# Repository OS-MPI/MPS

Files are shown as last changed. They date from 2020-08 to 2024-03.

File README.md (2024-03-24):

# The Magnetic Particle Spectroscopy (MPS) device
# [Link to the wiki](https://github.com/OS-MPI/MPS/wiki)
# [Link to the Main OS-MPI Page](https://os-mpi.github.io/)

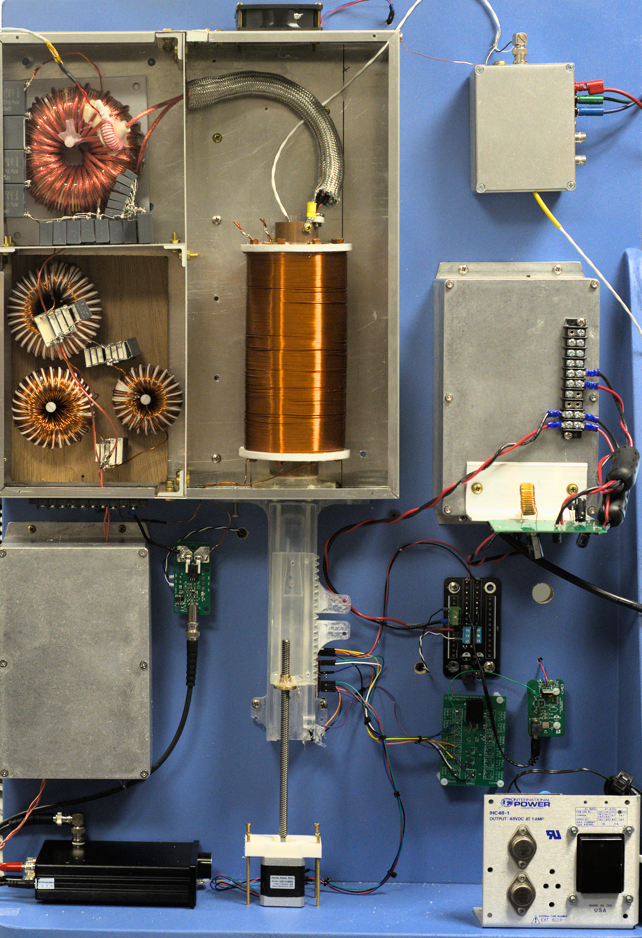
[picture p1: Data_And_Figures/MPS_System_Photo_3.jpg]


## Motivation and Introduction

The system we are calling the MPS device is a low cost, and fairly simple to manufacture project which more generally speaking is a platform designed around understanding magnetic characteristics of superparamagentic iron oxide nanoparticles (SPIONs). The motivation was to condense the numerous existing systems into a singlular platform capable of providing insights into the nanoparticles irrespective of the specific goal of the lab. With that in mind, calling our platform an "MPS" system is rather imprecise; while one mode is traditional "spectroscopy" the device is designed to be flexible and able to perform relaxometry measurements as well as magnetometry, yet in order to give the project an easy-to-find, descriptive name, we settled on the "magnetic particle spectroscopy" system. 

## State of the project

In the current state (of March 2024) we have the system working in all [primary operational modes](https://github.com/OS-MPI/MPS/wiki/Modes-of-operation). It is capable of sensitively detecting SPIONs to the ng Fe level, quantifying the magnetization spectra, tracing the hysteresis loops, etc. 

The primary focus now is improving the documentation.

## System overview

Broadly speaking, there are four principle hardware components, the three coils (drive, receive, and bias) and the sample positioner. The drive coils produce magnetic fields (typ. 10 mT) which cause the SPIONs within the bore to go into and out of saturation at 23.8 kHz. This changing magnetism induces a voltage in the receive coils. The bias coils allow for the quasistatic operating point of the SPIONs to be modulated by generating low frequency (~10 Hz) fields up to about 50 mT.

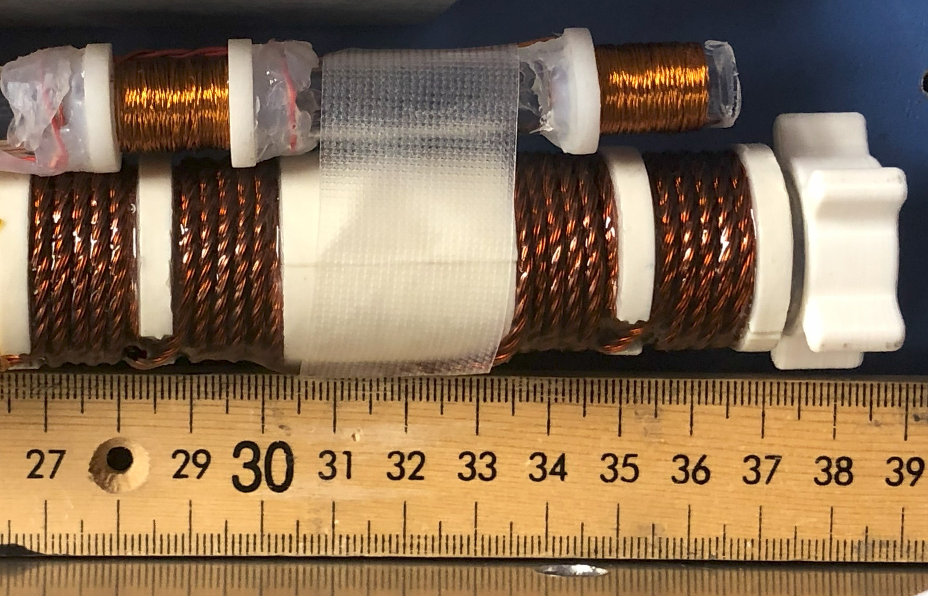
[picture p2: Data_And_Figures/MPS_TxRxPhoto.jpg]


### Drive/Transmit system
The drive system consists of the drive coils as well as the amplifier and filter. 

The drive coil is seen in the photograph above (the larger coil with four sub-sections). All of the four winding sections are in the same handedness. See the Wiki for further details. 

In this photograph, we utilize an in-house made Litz wire (18 strands of 28 AWG magnet wire), although other Litz wires may work similarly well. Previously a commercial Litz wire with 115 strands of 36AWG was used, but because of the plastic sleeve over the wires, they could not be easily stabilized with epoxy. 

The drive filter serves to purify and the waveform produced by the amplifier. Most amplifiers produce about 0.1% (or worse) total harmonic distortion, so without this filter those amplifier-generated distortions will dominate the noise floor. That being said, its among the most challenging components to manufacture, so its worth discussing which components are essential, and which are more or less optional. Refering to the schematic below, the two most important sections are the tuning/matching capacitors (C1 and C2), and the transformer (LPri and LSec). The tuning capacitors form a resonant circuit with Ldrive (the drive coil's equivalent load). This can be seen if you notice the loop formed by C1 C2 and LDrive is resonant. The choice of values for C1 and C2 is to make the equivalent impedance 8 ohms or so. The transformer should be a ferrite such as N87 and be designed such that the core flux is well below saturation (~20x lower, so 20ish mT). The purpose is to mitigate common-mode noise and provide isolation/break any ground loops. The other filter components can be "dropped in" later without disturbing the overall circuit. But these additional filtering components are both the most challenging to build, and less necessary. 
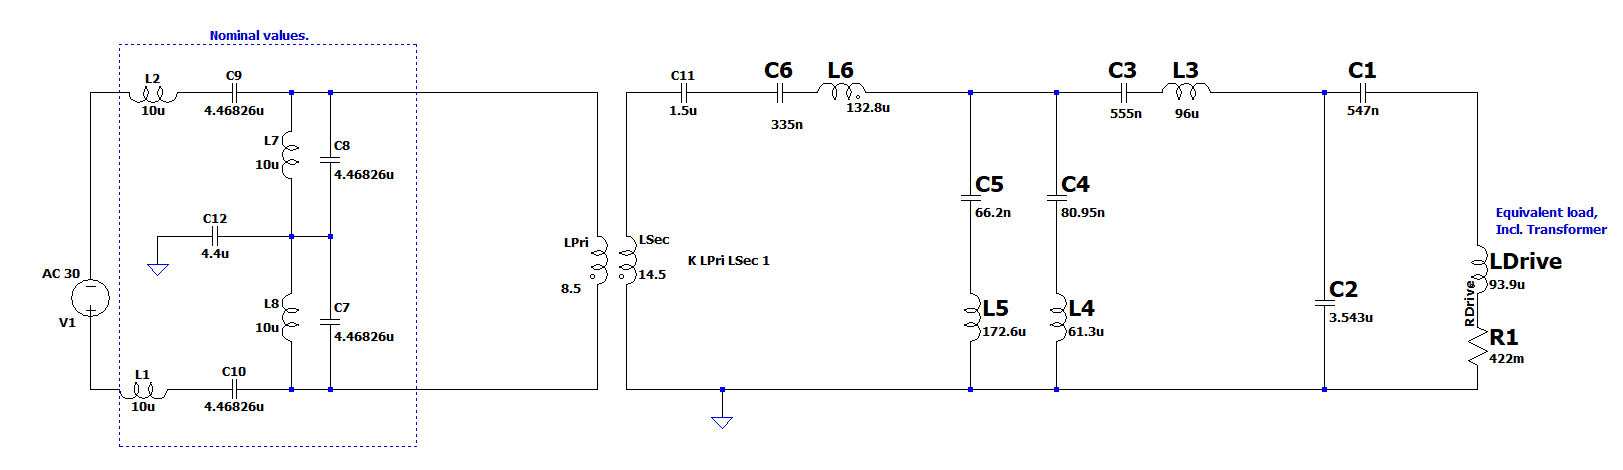
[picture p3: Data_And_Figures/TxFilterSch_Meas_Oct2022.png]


Many different drive amplifiers can be used. We have used both linear and switch-mode amplifiers with success. For a basic system, the AIYIMA A07 can be used, or other amplifiers based on the TPA3255 will likely be good choices. For example Nobsound G2 pro is also likely good and is pre-configured to be in PBTL mode. That IC from Texas Instruments has excellent performance given the cost and high switching frequency. The AE Techron 7224 is considerably more expensive, but produces a much higher fidelity waveform and has far more power available.

### Receive system

The receive system consists of the gradiometer receive coils, the filter, matching transformer, and preamplifier. The receive coil is a simple gradiometer to mitigate the net voltage induced from the changing magnetic drive fields (60-80 dBc attenuation of the voltage is a reasonable target). The filter reduces the amplitude of the signal at the drive frequency, but doesnt fully remove it. The matching transformer steps up the voltage produced by the receive coil (post filter) to improve the noise performance of the system. The transformer also provides isolation and common-mode supression, which help signal fidelity. The preamplifier amplifies the signal to a level more usable by the data acquisition hardware. In our case, we digitize the signals with a National Instruments NI PXIe 6363 and 6361. 

### Bias system
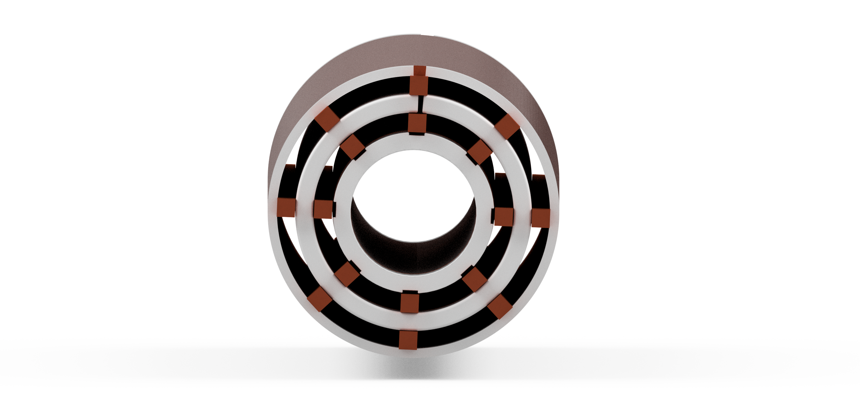
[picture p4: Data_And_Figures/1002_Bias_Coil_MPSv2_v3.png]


The bias system applies a low frequency (~10Hz), high amplitude waveform to probe the magnetization response at different quasistatic operating points. "Quasistatic" is emphasized here just because we utilize the assumption that this frequency is so low relaxation effects are negligible.

The system was initially designed to allow for even very small SPIONs (e.g. 5nm) to be probed out toward saturation, so many turns were added and cooling spaces were added to allow air to pass between the windings. With this design, passive convection is sufficient for normal operation at 50 mT peak. For up to 100 mT peak, lower duty cycles, or forced air should be used. 

This coil can be neglected if only hysteresis loop tracing or spectroscopy modes will be used. In that case, the diameter of the shielding tube should be increased to about 50-60 mm diameter. 

### Sample positioner

An automatic sample positioner is used to allow for consistent placement of the SPIONs as well as having the sample move in and out repeatedly to allow for multiple baselines to acquired. 

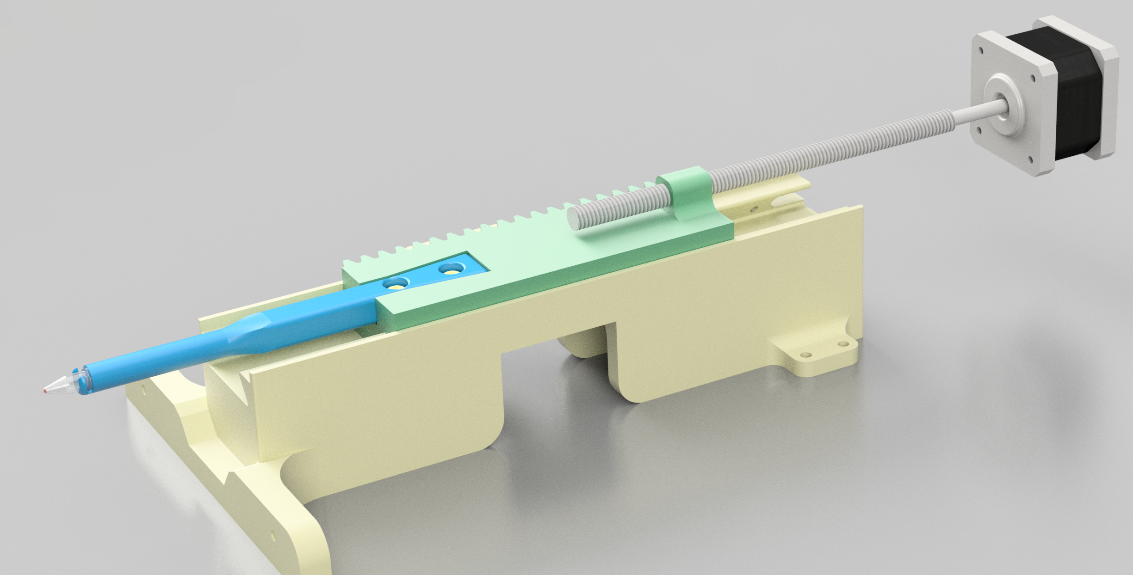
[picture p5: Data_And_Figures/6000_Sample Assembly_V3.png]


### Software

The software is written with LabVIEW 2021. Labview is not backwards compatible, so it must be operated with version 2021 or newer. 

With any issues regarding the project or missing files/documentation, [please reach out to the authors of this project here](https://github.com/OS-MPI/MPS/wiki/Contact-Us).

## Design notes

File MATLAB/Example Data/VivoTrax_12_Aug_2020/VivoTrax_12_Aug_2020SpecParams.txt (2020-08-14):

SpecParams,SpecVals
Sampling Freq.,1000000
Interpolated Freq.,996300
Drive Freq.,24300
Drive Amplitude (mT),4.5178
Drive Amplitude (Volts),0.32073
Drive Amplifier Name,OPA549_Single_BoardRev2
Drive Current Monitor Volts Per Amp,0.1
Drive Field mT per Amp,2
Power Supply Name,Tenma 72-7245
Pre-Amplifier Name,INA217 V0
Pre-Amplifier Gain,100
Test Time,2
Number of Averages,2
NonLinearity Index (F1/F3),7.755

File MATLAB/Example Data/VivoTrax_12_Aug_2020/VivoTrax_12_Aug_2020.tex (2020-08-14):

\documentclass{article}
\usepackage[utf8]{inputenc}
\usepackage{graphicx}
\title{ADD TITLE}
\date{\today}
\begin{document}
\section{Acquisition Parameters}
\begin{itemize}	\item{\textbf{Particle Name}:VivoTrax}
	\item{\textbf{Particle Manufacturer}:Magnetic Insight}
	\item{\textbf{SPION Lot}:}
	\item{\textbf{SPION Mfg. Date}:}
	\item{\textbf{SPION Core Size}:999}
	\item{\textbf{SPION Hydrodynamic Diameter}:999}
	\item{\textbf{Concentration}:5.5}
	\item{\textbf{Sample Volume}:0.018}
	\item{\textbf{SPION Coating}:}
	\item{\textbf{Notes}:There is a small bubble}
	\item{\textbf{User Name}:Eli Mattingly}
	\item{\textbf{User Location}:Martinos Center, Boston, MA, USA}
	\item{\textbf{Total Acquisition Time (Seconds)}:168.9575}
\end{itemize}
\begin{figure}[h] 
 \centering 
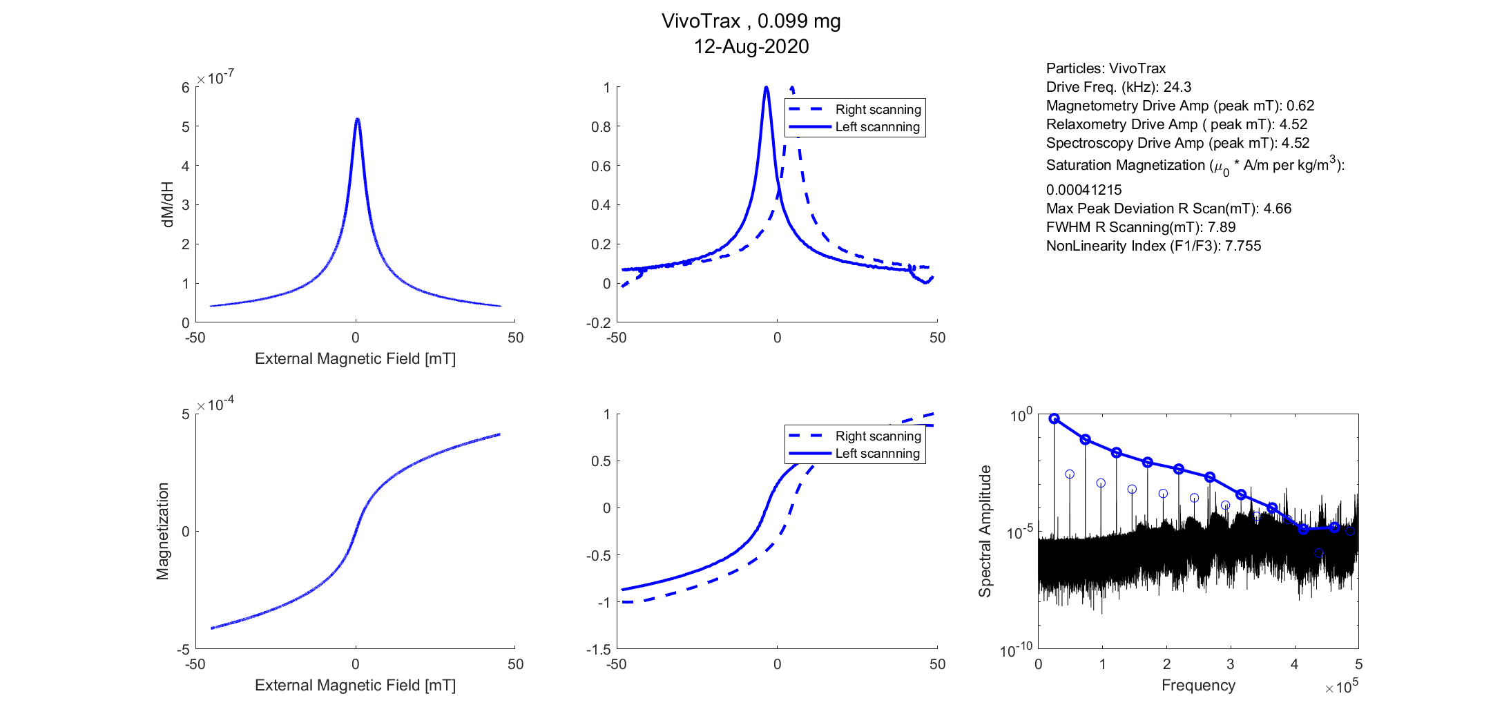
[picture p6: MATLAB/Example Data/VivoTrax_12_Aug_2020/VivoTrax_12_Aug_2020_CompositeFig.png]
 
 \caption{A summary of the experiment}
 \end{figure}
\section{Magnetometry}

\begin{itemize}	\item{\textbf{Sampling Freq.}:1000000}
	\item{\textbf{Interpolated Freq.}:996300}
	\item{\textbf{Drive Freq.}:24300}
	\item{\textbf{Bias Freq.}:20}
	\item{\textbf{Bias Waveform Shape}:Sine}
	\item{\textbf{Bias Amplitude (mT)}:45.1291}
	\item{\textbf{Bias Amplitude (Volts)}:1.7495}
	\item{\textbf{Bias Amplifier Name}:RCF IPS700}
	\item{\textbf{Bias Current Monitor Volts Per Amp}:0.04}
	\item{\textbf{Bias Field mT per Amp}:6}
	\item{\textbf{Drive Amplitude (mT)}:0.62081}
	\item{\textbf{Drive Amplitude (Volts)}:0.042764}
	\item{\textbf{Drive Amplifier Name}:OPA549_Single_BoardRev2}
	\item{\textbf{Drive Current Monitor Volts Per Amp}:0.1}
	\item{\textbf{Drive Field mT per Amp}:2}
	\item{\textbf{Power Supply Name}:Tenma 72-7245}
	\item{\textbf{Pre-Amplifier Name}:INA217 V0}
	\item{\textbf{Pre-Amplifier Gain}:100}
	\item{\textbf{Test Time}:2}
	\item{\textbf{Number of Averages}:2}
	\item{\textbf{Saturation Magnetization (\mu_0 * A/m per kg/m^3)}:0.00041215}
\end{itemize}
\begin{figure}[h] 
 \centering 
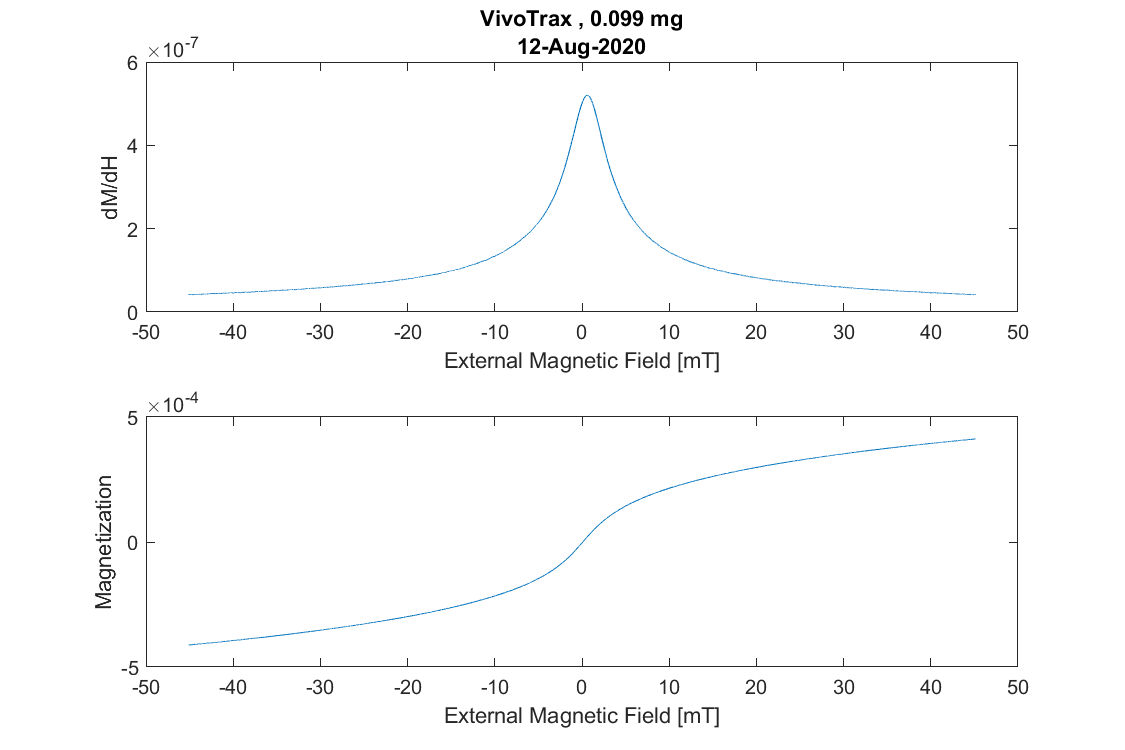
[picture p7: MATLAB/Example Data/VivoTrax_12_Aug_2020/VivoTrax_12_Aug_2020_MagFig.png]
 
 \caption{TestCaption for Mag}
 \end{figure}
\section{Relaxometry}
\begin{itemize}
\section{Magnetometry}

\begin{itemize}	\item{\textbf{Sampling Freq.}:1000000}
	\item{\textbf{Interpolated Freq.}:996300}
	\item{\textbf{Drive Freq.}:24300}
	\item{\textbf{Bias Freq.}:20}
	\item{\textbf{Bias Waveform Shape}:Sine}
	\item{\textbf{Bias Amplitude (mT)}:45.033}
	\item{\textbf{Bias Amplitude (Volts)}:1.7495}
	\item{\textbf{Bias Amplifier Name}:RCF IPS700}
	\item{\textbf{Bias Current Monitor Volts Per Amp}:0.04}
	\item{\textbf{Bias Field mT per Amp}:6}
	\item{\textbf{Drive Amplitude (mT)}:4.5202}
	\item{\textbf{Drive Amplitude (Volts)}:0.32073}
	\item{\textbf{Drive Amplifier Name}:OPA549_Single_BoardRev2}
	\item{\textbf{Drive Current Monitor Volts Per Amp}:0.1}
	\item{\textbf{Drive Field mT per Amp}:2}
	\item{\textbf{Power Supply Name}:Tenma 72-7245}
	\item{\textbf{Pre-Amplifier Name}:INA217 V0}
	\item{\textbf{Pre-Amplifier Gain}:100}
	\item{\textbf{Test Time}:2}
	\item{\textbf{Number of Averages}:2}
	\item{\textbf{Max Peak Deviation R Scan(mT)}:4.6556}
	\item{\textbf{Max Peak Deviation L Scan(mT)}:-3.3237}
	\item{\textbf{FWHM R Scanning(mT)}:7.8939}
	\item{\textbf{FWHM L Scanning(mT)}:7.9373}
\begin{figure}[h] 
 \centering 
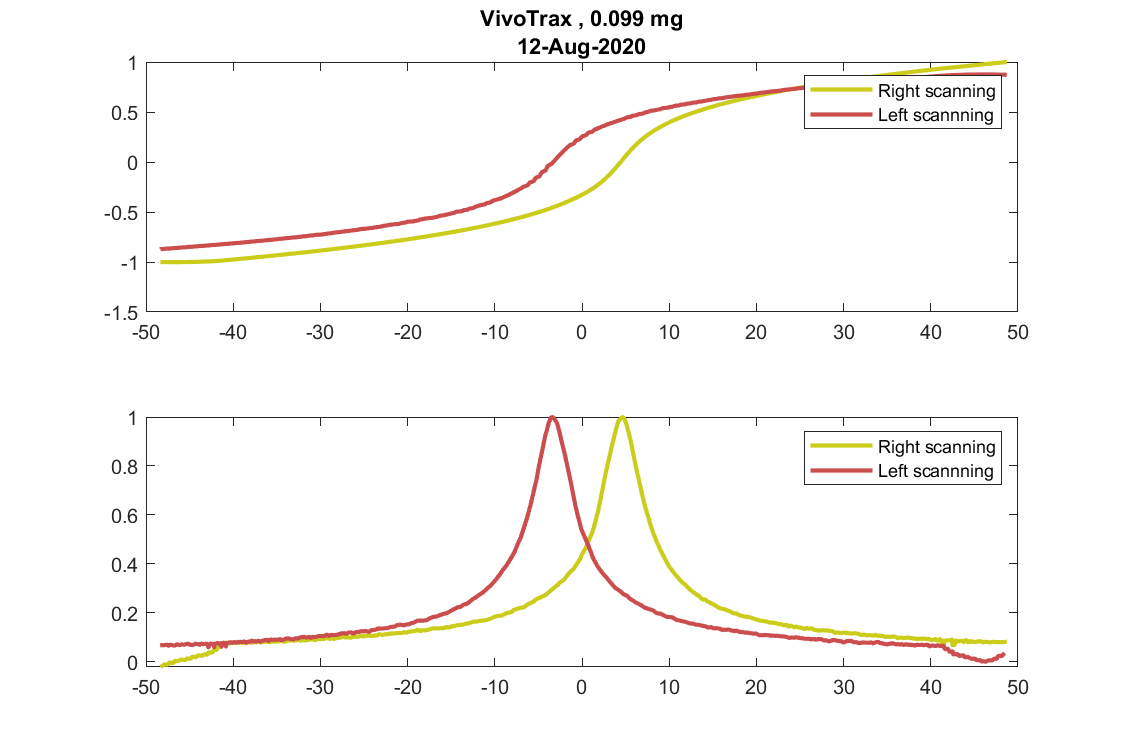
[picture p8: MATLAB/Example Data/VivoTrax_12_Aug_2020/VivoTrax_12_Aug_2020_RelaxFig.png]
 
 \caption{Results from the relaxometry experiment}
 \end{figure}\end{itemize}

\section{Spectroscopy}
\begin{itemize}	\item{\textbf{Sampling Freq.}:1000000}
	\item{\textbf{Interpolated Freq.}:996300}
	\item{\textbf{Drive Freq.}:24300}
	\item{\textbf{Drive Amplitude (mT)}:4.5178}
	\item{\textbf{Drive Amplitude (Volts)}:0.32073}
	\item{\textbf{Drive Amplifier Name}:OPA549_Single_BoardRev2}
	\item{\textbf{Drive Current Monitor Volts Per Amp}:0.1}
	\item{\textbf{Drive Field mT per Amp}:2}
	\item{\textbf{Power Supply Name}:Tenma 72-7245}
	\item{\textbf{Pre-Amplifier Name}:INA217 V0}
	\item{\textbf{Pre-Amplifier Gain}:100}
	\item{\textbf{Test Time}:2}
	\item{\textbf{Number of Averages}:2}
	\item{\textbf{NonLinearity Index (F1/F3)}:7.755}
\begin{figure}[h] 
 \centering 
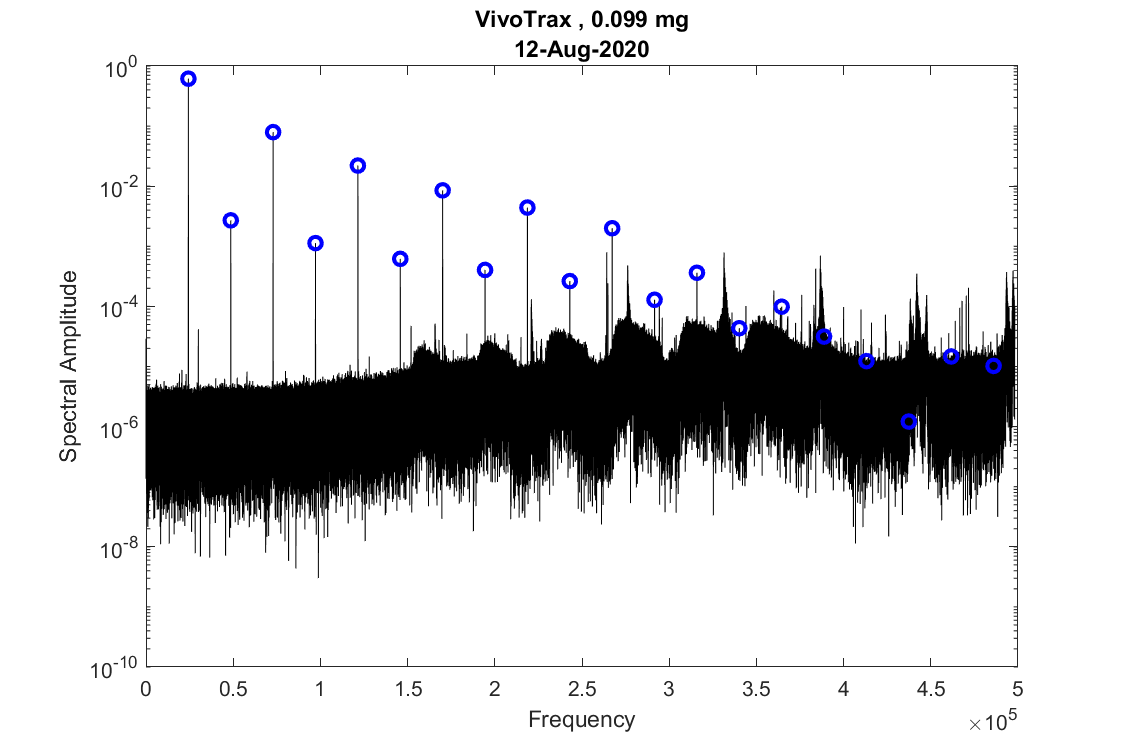
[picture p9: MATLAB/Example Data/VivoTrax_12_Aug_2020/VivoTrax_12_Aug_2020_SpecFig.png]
 
 \caption{Results from the spectroscopy}
 \end{figure}\end{itemize}

\end{document}

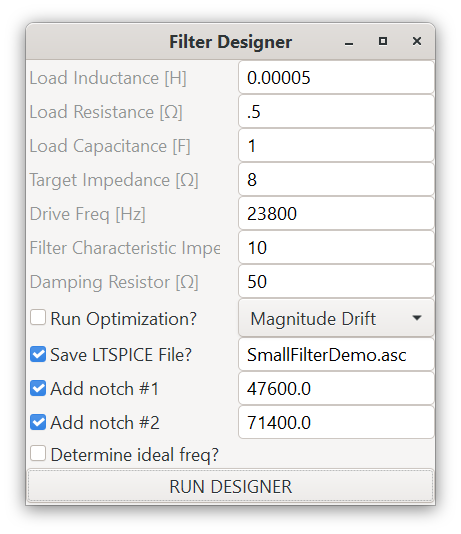
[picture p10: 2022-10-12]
Electrical Hardware/Filter Demo Files/Filter design GUI.PNG

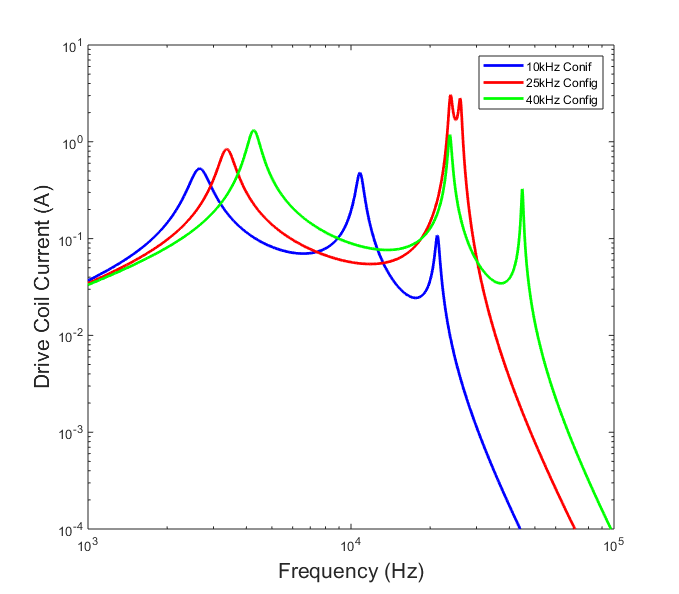
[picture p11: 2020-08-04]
Electrical Hardware/LTSpice Files/Drive Filter/Configs_TransferFunctions_VinToDriveCurrent.png

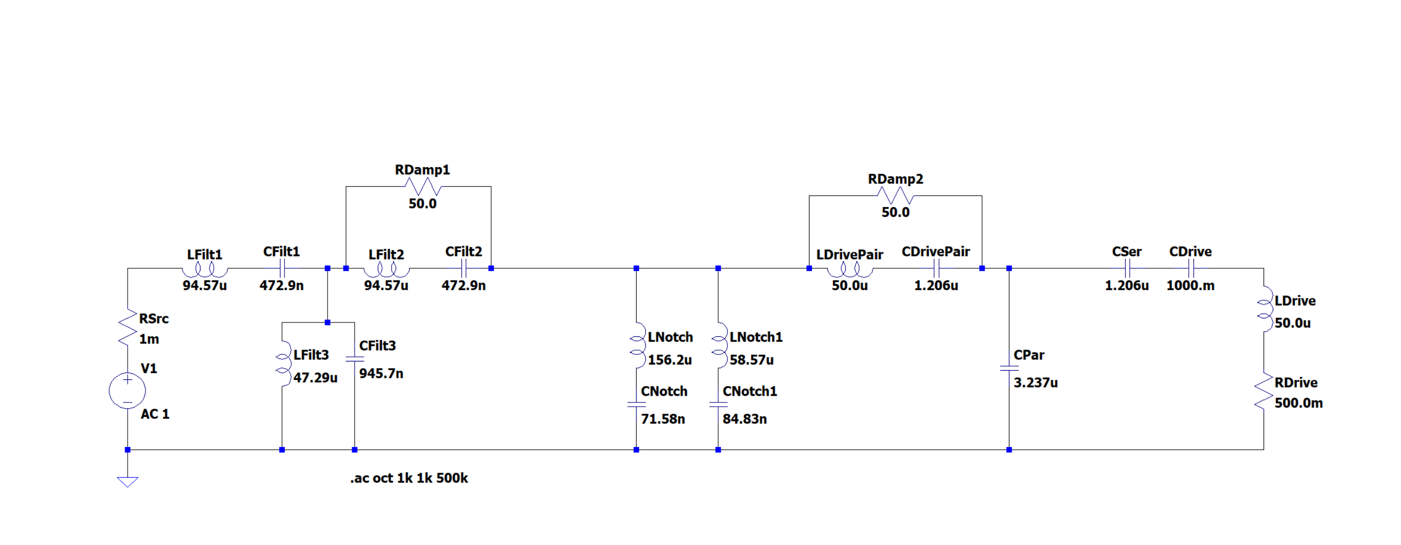
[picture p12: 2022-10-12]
Electrical Hardware/Filter Demo Files/Filter design GUI_Output.PNG

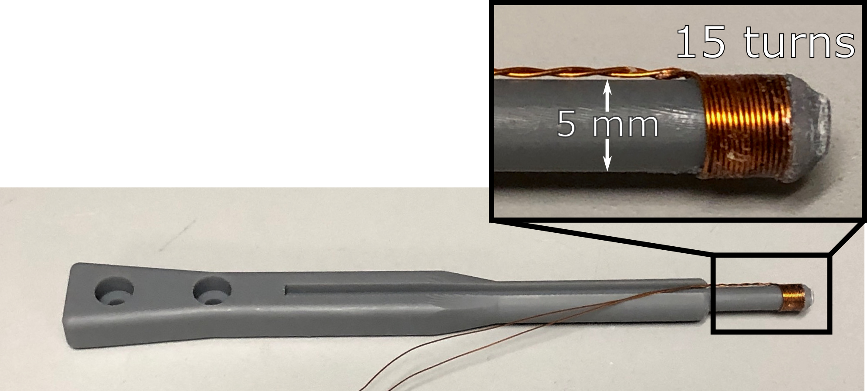
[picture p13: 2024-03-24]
Data_And_Figures/CalibCoilFig.png

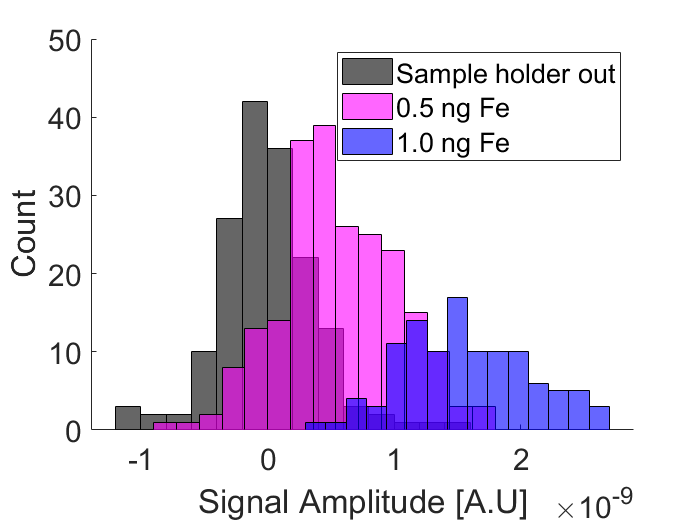
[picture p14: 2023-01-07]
Data_And_Figures/Synomag_Hist_0,5ng_1ng.png

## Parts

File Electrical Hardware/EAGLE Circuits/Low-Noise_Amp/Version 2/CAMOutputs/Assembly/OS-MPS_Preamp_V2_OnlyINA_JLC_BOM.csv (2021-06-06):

Comment | Designator | Package | LCSC Part | 2
2.2k | R2,R3,R7,R8,R32,R33 | R0805 | C17520
0 | R9,R10 | R0805 | C17477
 | LED1,LED2 | SML0805 | C84256
100 | R1,R4,R5,R6,R31 | R0805 | C17408
 | D3,D4 | SOD-123 | C64898
100n | C6,C7 | C1206 | C24497
1n | C5 | C1206 | C35216
SWS004 | S1 | SMS-004 | C3693
1u | C3,C4,C13,C14 | C1206 | C1848

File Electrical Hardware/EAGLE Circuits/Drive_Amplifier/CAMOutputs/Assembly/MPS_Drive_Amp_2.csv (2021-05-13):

Qty | Value | Device | Package | Parts | Description | DATASHEET_URL | DESCRIPTION | FAMILY_NAME | GENERIC_PART_NUMBER | INDUSTRY_STD_PKG_TYPE | MANUFACTURER | MANUFACTURER_PART_NUMBER | MF | MPN | OC_FARNELL | OC_NEWARK | PACKAGE_DESIGNATOR | PIN_COUNT | POPULARITY | SPICEPREFIX | TP_SIGNAL_NAME | VENDOR
1 |  | LEDCHIPLED_0805 | CHIPLED_0805 | LED1 | LED |  |  |  |  |  |  |  |  |  |  |  |  |  | 52
2 |  | PINHD-1X2 | 1X02 | JP1, JP2 | PIN HEADER |  |  |  |  |  |  |  |  |  |  |  |  |  | 98
3 |  | W237-102 | W237-102 | V+TERM, VINTERM, VOUT_TERM | WAGO SCREW CLAMP |  |  |  |  |  |  |  |  | 237-102 | unknown | 70K9898 |  |  | 32
8 | .1u | C-EUC1206 | C1206 | C4, C5, C6, C7, C8, C9, C10, C11 | CAPACITOR, European symbol |  |  |  |  |  |  |  |  |  |  |  |  |  | 54 | C
1 | 0.1 | R-EU_VTA52 | VTA52 | R4 | RESISTOR, European symbol |  |  |  |  |  |  |  |  |  |  |  |  |  | 0 | R
1 | 100k | R-US_R1206 | R1206 | R12 | RESISTOR, American symbol |  |  |  |  |  |  |  |  |  |  |  |  |  | 19 | R
1 | 100p | C-EUC1206 | C1206 | C3 | CAPACITOR, European symbol |  |  |  |  |  |  |  |  |  |  |  |  |  | 54 | C
1 | 100u | C-US050-025X075 | C050-025X075 | C1 | CAPACITOR, American symbol |  |  |  |  |  |  |  |  |  |  |  |  |  | 0 | C
1 | 10V | SCHOTTKY-DIODEDO35-7 | DO35-7 | D1 | Schottky Diode
1 | 10k | R-US_R1206 | R1206 | R9 | RESISTOR, American symbol |  |  |  |  |  |  |  |  |  |  |  |  |  | 19 | R
1 | 1u | C-EUC1206 | C1206 | C2 | CAPACITOR, European symbol |  |  |  |  |  |  |  |  |  |  |  |  |  | 54 | C
9 | 2.2k | R-US_R1206 | R1206 | R1, R2, R6, R8, R10, R11, R13, R14, R15 | RESISTOR, American symbol |  |  |  |  |  |  |  |  |  |  |  |  |  | 19 | R
2 | 22k | R-US_R1206 | R1206 | R5, R7 | RESISTOR, American symbol |  |  |  |  |  |  |  |  |  |  |  |  |  | 19 | R
1 | 3V | SCHOTTKY-DIODEDO35-7 | DO35-7 | D3 | Schottky Diode
1 | 4.7k | R-US_R1206 | R1206 | R3 | RESISTOR, American symbol |  |  |  |  |  |  |  |  |  |  |  |  |  | 19 | R
1 | 78L12F | 78L12F | SOT89 | IC4 | POSITOIV-VOLTAGE REGULATORS |  |  |  |  |  |  |  |  |  |  |  |  |  | 0
1 | 7A | R-US_R1206 | R1206 | FUSE_1 | RESISTOR, American symbol |  |  |  |  |  |  |  |  |  |  |  |  |  | 19 | R
1 | INA105U | INA105U | SO08 | IC1 | Precision Unity Gain Diff. Amplifier |  |  |  |  |  |  |  | TEXAS INSTRUMENTS | INA105KU | 1754832 | 35C0475 |  |  | 0
1 | LM358MX | LM358MX | SO08 | IC2 | OP AMP also LM158, LM258, LM2904 |  |  |  |  |  |  |  |  |  |  |  |  |  | 0
1 | OPA549T | OPA549T | KV11 | U1 |  | http://www.ti.com/lit/gpn/OPA549 | High-Voltage, High-Current Op Amp, Excellent Output Swing | HIGH OUTPUT CURRENT | OPA549 | TO-220 | Texas Instruments | OPA549T |  |  |  |  | KV | 11 |  |  |  | Texas Instruments
1 | SPD30P06PTO252 | SPD30P06PTO252 | TO252 | Q1 | SIPMOS(R) Power-Transistor P-Channel, Enhancement mode |  |  |  |  |  |  |  |  |  |  |  |  |  | 3
11 | TPTP20SQ | TPTP20SQ | TP20SQ | TP1, TP2, TP3, TP4, TP5, TP6, TP7, TP8, TP9, TP10, TP11 | Test pad |  |  |  |  |  |  |  |  |  |  |  |  |  | 2

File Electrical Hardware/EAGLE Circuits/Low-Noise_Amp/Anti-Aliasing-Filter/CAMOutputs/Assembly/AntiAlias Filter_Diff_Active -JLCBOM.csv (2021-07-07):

Value | Designator | Package | LCSC Part
 | LED1, LED2 | CHIPLED_1206
10u | C3, C4, C19, C20 | C1206
0 | R5, R13 | R1206
100k | R7, R12 | R1206
10u |  | C1210
1n | C2, C8, C9, C10, C12, C14, C16, C17 | C1206
2.2k | R8, R9 | R1206
270u | L1, L2, L3, L4 | L1812 | C394138
3n | C1,C13 | C1206 | C141013
470 | R1, R2, R3, R4, R10, R11, R15, R16 | R1206
47n | C7, C18,C11, C15 | C1210 | C342651
78L05F | IC1 | SOT89 | C181132
79LXX | U$1 | SOT89 | C122849
TLC082IDR | U1 | SO8_DIO-M | C7710

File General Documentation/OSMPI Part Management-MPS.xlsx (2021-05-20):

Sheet: MPS
Magnetic Particle Spectroscopy Project Management Spreadsheet |  |  |  |  |  |  |  |  |  |  |  |  |  |  |  |  |  |  |  |  | Drop-down menu source:
 |  |  |  |  |  |  |  |  |  |  |  |  |  |  |  |  |  |  |  |  | Yes | CNC Milling
Part Number (3-####) |  |  |  |  | Part Name | Quantitiy | Material | Designed (.5 = Drawn, 1 = Drawn& Saved properly) | Fabricated/Purchased | Assembled | Notes | Made in lab | Method of Mfg | Quoted (& Quote No.) | Paid | P.O. Number | Part Mass | Total Mass (kg) | Cost (USD) | Total Cost (USD) | No | 3D Print
 |  |  |  |  |  | 89 |  | 100.00% | 100.00% | 100.00% |  |  |  |  |  |  |  | 0.00 |  | $3299.54
1 | 0 | 0 | 0 |  | Transmit Assembly | 1 | N/A |  |  |  |  | Yes |  | N/A | N/A | N/A |  |  | N/A | N/A
1 | 1 | 0 | 0 |  | Transmit Enclosure | 1 | Aluminum | 1 | 1 | 1 | Digikey No. HM2783-ND | No |  | N/A | N/A | N/A |  |  | $74.99 | $74.99
1 | 1 | 0 | 0 |  | Enclosure Lid | 1 | Aluminum | 1 | 1 | 1 |  | No |  |  |  |  |  |  | $20.01 | $20.01
1 | 2 | 0 | 0 |  | Tx Filter
1 | 2 | 1 | 0 |  | Tx Inductors
1 | 2 | 1 | 1 |  | L1 |  |  | 1 | 1 | 1 | Hand- wound toroid. Passive air cooled | Yes | 3D Print |  |  |  |  |  |  | N/A
1 | 2 | 1 | 2 |  | L2 |  |  | 1 | 1 | 1 | Hand- wound toroid. Passive air cooled | Yes | 3D Print |  |  |  |  |  |  | N/A
1 | 2 | 2 | 0 |  | Tx Capacitors
1 | 2 | 2 | 1 |  | C2A (10kHz) | 1 |  | 1 | 1 | 1 | 11uF (Measured part says 10uF) Similar to Digikey no. 399-13087-ND | No |  |  |  |  |  |  | $5.70 | $5.70
1 | 2 | 2 | 2 |  | C2B (25kHz) | 1 |  | 1 | 1 | 1 | 5uF | No |  |  |  |  |  |  | $8.17 | $8.17
1 | 2 | 2 | 3 |  | C2C (40kHz) | 1 |  | 1 | 1 | 1 | 1uF - Equivalent part is Digikey No. 399-13087-ND (we used 3x 338-3945-ND due to availability) | No |  |  |  |  |  |  | 1.08 | 1.08
1 | 2 | 2 | 4 |  | C3A | 1 |  | 1 | 1 | 1 | 5uF - Digikey Part No. 338-3943-ND | No |  |  |  |  |  |  | 8.17 | 8.17
1 | 2 | 2 | 5 |  | C3B | 1 |  | 1 | 1 | 1 | 0.94uF - Measured | No |  |  |  |  |  |  | 1.08 | 1.08
1 | 2 | 2 | 6 |  | C3C | 1 |  | 1 | 1 | 1 | 1uF | No |  |  |  |  |  |  | 1.08 | 1.08
1 | 3 | 0 | 0 |  | Drive Coil
1 | 3 | 1 | 0 |  | Drive Coil Assm |  |  | 1 | 1 | 1
1 | 3 | 1 | 1 |  | Drive Coil Main Body | 1 | ABS | 1 | 1 | 1
1 | 3 | 1 | 2 | A/B | Drive Coil Second Layer | 1 | ABS | 1 | 1 | 1
1 | 3 | 1 | 3 |  | Drive Coil End | 1 | ABS | 1 | 1 | 1
1 | 4 | 0 | 0 |  | Bias Coil
1 | 4 | 0 | 1 |  | Bias Coil Wire | 1 | Cu | 1 | 1 | 1 | Cost is based on approximately $15 per lb of wire | No |  |  |  |  |  |  | $18.00 | $18.00
1 | 4 | 0 | 2 |  | Bias Coil Spacer | 16 | ABS | 1 | 1 | 1
1 | 5 | 0 | 0 |  | Commerical Electronics
1 | 5 | 1 | 0 |  | Power Supplies
1 | 5 | 1 | 1 |  | Power Supply - DC Bias | 2 |  | 1 | 1 | 1 | Digikey No. 285-1815-ND - NOT USED IN CURRENT CONFIG | No |  |  |  |  |  |  | $0.00 | $0.00
1 | 5 | 1 | 2 |  | Power Supply - Drive | 1 |  | 1 | 1 | 1 | Digikey No. 1145-1101-ND | No |  |  |  |  |  |  | $63.47 | $63.47
1 | 5 | 2 | 0 |  | Power Amplifier-Drive (PCB) | 1 |  | 1 | 1 | 1 | From PCBWay, cost for 5EA | No |  |  |  |  |  |  | $23.00 | $23.00
1 | 5 | 2 | 1 |  | OPA549 | 1 |  | 1 | 1 | 1 | Digikey part no. OPA549T-ND | No |  |  |  |  |  |  | $22.93 | $22.93
1 | 5 | 2 | 2 |  | MOSFET P-CH, Rev Vol. Protection | 1 |  | 1 | 1 | 1 | Digikey part no. DMP4015SK3-13DICT-ND |  |  |  |  |  |  |  | $0.83 | $0.83
1 | 5 | 2 | 3 |  | INA105 Buffer | 0 |  |  |  |  | Part of current sense. Not used actively
1 | 5 | 2 | 4 |  | Current Sense R | 1 |  | 1 | 1 | 1 | Digikey Part No. 15FR100E-ND |  |  |  |  |  |  |  | $3.08 | $3.08
1 | 5 | 3 | 0 |  | Power Amplifier Bias | 1 |  |  |  |  | RCF IPS 700 2 x 300 W Class AB Professional Power Amplifier | No |  |  |  |  |  |  | $418.00 | $418.00
2 | 0 | 0 | 0 |  | Rx Assembly
2 | 1 | 0 | 0 |  | Rx Coil Assembly
2 | 1 | 0 | 1 |  | Rx Coil Body | 1 |  | 1 | 1 | 1 |  | Yes | 3D Print |  |  |  |  |  |  | N/A
2 | 1 | 1 | 1 |  | Threaded Rod | 1 |  | 1 | 1 | 1 |  | Yes | 3D Print |  |  |  |  |  |  | N/A
2 | 1 | 1 | 2 |  | Adjustment Nut | 1 |  | 1 | 1 | 1 |  | Yes | 3D Print |  |  |  |  |  |  | N/A
2 | 1 | 1 | 3 |  | Nut Stop Plate | 2 |  | 1 | 1 | 1 |  | Yes | 3D Print |  |  |  |  |  |  | N/A
2 | 1 | 1 | 4 |  | Nut Plate Support | 2 |  | 1 | 1 | 1 |  | Yes | 3D Print |  |  |  |  |  |  | N/A
2 | 1 | 1 | 5 |  | Ball Bearings | 20 |  | 1 | 1 | 1 | McMaster Part No. 9614K52 | No |  |  |  |  |  |  | $0.02 | $0.48
2 | 2 | 0 | 0 |  | Rx Low Noise Amp |  |  | 1 | 1 | 1
2 | 2 | 1 | 0 |  | Rx LNA PCB | 1 |  | 1 | 1 | 1 | From PCBWay, price is for 5EA, shipped |  |  |  |  |  |  |  | $23.00 | $23.00
2 | 2 | 2 | 0 |  | INA217 Instr Amp | 1 |  | 1 | 1 | 1 | Digikey Part No. 296-13452-5-ND |  |  |  |  |  |  |  | $6.74 | $6.74
2 | 2 | 0 | 0 |  | Coil Housing |  |  |  |  |  | All Laser cut wood
2 | 2 | 0 | 1 |  | Housing Bottom | 1 | Plywood | 1 | 1 | 1 |  | Yes |  |  |  |  |  |  |  | N/A
2 | 2 | 0 | 2 |  | Housing Side | 2 | Plywood | 1 | 1 | 1 |  | Yes |  |  |  |  |  |  |  | N/A
2 | 2 | 0 | 3 |  | Housing Back | 1 | Plywood | 1 | 1 | 1 |  | Yes |  |  |  |  |  |  |  | N/A
2 | 2 | 0 | 4 |  | Housing Front | 1 | Plywood | 1 | 1 | 1 |  | Yes |  |  |  |  |  |  |  | N/A
2 | 2 | 0 | 5 |  | Terminal Block | 2 | Plywood | 1 | 1 | 1 | McMaster Part No. 7527K44 | No |  |  |  |  |  |  | $2.24 | $4.48
2 | 2 | 0 | 6 |  | Housing Feet | 4 | Rubber | 1 | 1 | 1 | McMaster Part No. 9540K723 or equivalent | No |  |  |  |  |  |  | $0.32 | $1.30
2 | 2 | 0 | 7 |  | Cu Tube | 1 | Cu | 1 | 1 | 1 | McMaster Part No. 5175K139 or equivalent | No |  |  |  |  |  |  | $24.91 | $24.91
2 | 2 | 0 | 8 |  | Back Plate Groove | 2 | ABS | 1 | 1 | 1
2 | 2 | 0 | 9 |  | Tube Flange |  |  | 1 | 1 | 1
2 | 2 | 0 | 10 |  | Tube End Support | 1 | ABS | 1 | 1 | 1
3 | 0 | 0 | 0 |  | Sample Assembly
3 | 1 | 0 | 0 |  | Sample Rails
3 | 1 | 0 | 1 |  | Sample Rail Base |  |  |  |  |  |  | Yes | 3D Print |  |  |  |  |  |  | N/A
3 | 1 | 0 | 2 |  | Sample Dovetail Slider |  |  |  |  |  |  | Yes | 3D Print |  |  |  |  |  |  | N/A
3 | 1 | 0 | 3 |  | Bulb Arm |  |  |  |  |  |  | Yes | 3D Print |  |  |  |  |  |  | N/A
3 | 2 | 0 | 0 |  | Motor and Driving
3 | 2 | 1 | 0 |  | Stepper Motor Parts
3 | 2 | 1 | 1 |  | Stepper Motor | 1 |  |  |  |  | SparkFun Part No. 9238 (other cheaper alternatives such as Sparkfun Part no. 10551) | No |  |  |  |  |  |  | $15.95 | $15.95
3 | 2 | 1 | 2 |  | Motor Driver | 1 |  |  |  |  | Sparkfun Part No. 12779 | No |  |  |  |  |  |  | $14.95 | $14.95
3 | 2 | 2 | 0 |  | Motor Mechanical Connectors
3 | 2 | 2 | 1 |  | Motor Pinion | 1 | Acetal | 1 | 1 | 1 | McMaster Part No. 2662N9 | No |  |  |  |  |  |  | $4.14 | $4.14
3 | 2 | 2 | 2 |  | Gear Rack | 1 | Acetal | 1 | 1 | 1 | McMaster Part No. 2662N52 or similar | No |  |  |  |  |  |  | $4.00 | $4.00
3 | 2 | 2 | 3 |  | Motor Bracket | 1 | Aluminum | 1 | 1 | 1 | Made from Alum for heat sinking with CNC, could also be 3D printed, though if possible I would reccomend including a heat sink somehow. | Yes
9 | 9 | 9 | 0 |  | Misc Expenses |  |  |  |  |  | This section is to budget in misc expenses which are hard to include explicitly with the part
9 | 9 | 9 | 1 |  | 3D Print Material | 1 |  |  |  |  | Amount of filament depends on which printer and settings are used. For now, I'll assume 1kg is sufficient as nothing needs to be printed solidly. Price is from Amazon (1.75mm ABS) | No |  |  |  |  |  |  | $20.00 | $20.00
9 | 9 | 9 | 2 |  | Plywood | 1 |  |  |  |  | Cost is based on ~2' x 4' of 1/4" thick plywood from local store - This will be enough with plenty to spare | No |  |  |  |  |  |  | $10.00 | $10.00
9 | 9 | 9 | 3 |  | NI Data Acquisition | 1 |  |  |  |  | Currently we use NI-USB-6363. Previously used a NI-USB-6211 ($1000) | No |  |  |  |  |  |  | $2500.00 | $2500.00

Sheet: Preamp
Qty | Value | Device | Package | Parts | Description | Notes | Vendor/PN | Vendor URL | Item URL | Column1
2 |  | LEDSML0805 | SML0805 | LED1, LED2 | LED | Pick colors as wanted. Indication of power | Digikey/475-2488-1-ND
6 |  | PINHD-1X2 | 1X02 | JP1, JP2, VIN, VOUT, VS+, VS- | PIN HEADER | Do not populate-- use when debugging or direct soldering to input/output
4 |  | R-US_R0805 | R0805 | R1, R5, R6, R7 | RESISTOR, American symbol | Gain resistors. Use 50 Ohms, and then other values depending on what gain you want. See pg. 11 of INA217 datasheet | Digikey/
2 | .1u | C-EUC1206 | C1206 | C6, C7 | CAPACITOR, European symbol | Bypass Cap. Do not ignore | Digikey/478-11522-1-ND
2 | 0 | R-US_R0805 | R0805 | R9, R10 | RESISTOR, American symbol | Short out with either 0 Ohm resistor or wires | Digikey/2019-RK73Z2ARTTDCT-ND
2 | 10u | C-EUC1206 | C1206 | C13, C14 | CAPACITOR, European symbol | AC Coupling Cap. Use C0G/NP0 for minimal distortion, this is a minimum but pick value based on cutoff freq. | Digikey/445-180318-1-ND
2 | 1N4004 | 1N4004 | DO41-10 | D1, D2 | DIODE | Generic diode note polarity | Digikey/2368-1N4004-ND
2 | 1k | R-US_R0805 | R0805 | R2, R3 | RESISTOR, American symbol | Can use the 2.2k or 1k (current limiting for LED) | Digikey/
1 | 1n | C-EUC1206 | C1206 | C5 | CAPACITOR, European symbol | Not needed, but prevents high freq. noise. | Digikey/
2 | 1u | C-EUC1206 | C1206 | C3, C4 | CAPACITOR, European symbol | For bypass of power supply | Digikey/399-13001-1-ND
3 | 2.2k | R-US_R0805 | R0805 | R8, R32, R33 | RESISTOR, American symbol | To enable a DC path for bias current of INA. Not critical value | Digikey/RMCF0805FT2K20CT-ND
2 | 22u | CPOL-USTT2D6 | TT2D6 | C1, C2 | POLARIZED CAPACITOR, American symbol | Value is a minimum. POLARIZED-- DO NOT PUT IN BACKWARDS. Line indicates negative terminal | Digikey/399-6650-1-ND
2 | 50R | R-US_R0805 | R0805 | R4, R31 | RESISTOR, American symbol | For INA stability, can use lower precision (but they are cheap enough, and high precision should be used on gain resistors anyway) | Digikey/PAT49.9BCT-ND
1 |  |  |  | J1 | WR-SMA SMA PCB End Launch Jack | We don’t use. Instead direct solder wires |  |  | https://www.we-online.com/catalog/datasheet/60312202111527.pdf
2 |  | W237-102 | W237-102 | BATT+, BATT- | WAGO SCREW CLAMP | Direct solder battery wires if wanted, or use screw terminals
1 | INA217AIP | INA217AIP | P8 | U1 | INA217 Low noise INA | Low Noise, Low-Distortion Instrumentation Amplifier Replacement for SSM2017 |  |  | http://www.ti.com/lit/gpn/INA217
1 | SWS004 | SWS004 | SMS-004 | S1 | SMD Dip Switch 4 pol. | For gain selection | Digikey/360-3899-ND
2 |  |  |  | TP1, TP2 | Test pad | For use when debugging-- not necessary | Digikey/36-5019CT-ND
8 |  |  | 5019 | TP3, TP4, TP5, TP6, TP7, TP8, TP9, TP18 | https://www.digikey.com/en/products/detail/keystone-electronics/5019/3907343 |  | Digikey/296-13452-5-ND
Misc items:
Solder (lead free) | Digikey: SMDSWLF.015.3OZ-ND | Lead Free No-Clean, Water Soluble Wire Solder Sn96.5Ag3Cu0.5 (96.5/3/0.5) 27 AWG, 28 SWG Tube, 0.3 oz (8.51g)
Tweezers | Digkey/243-18851-ND
Flux | Digikey/KE1804-ND | FLUX PEN FORMULA 951 NO CLEAN

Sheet: Anti-Aliasing Filter
Qty | Value | Device | Package | Parts | Description | BUILT_BY | MANUFACTURER_PART_NUMBER | NOTE
2 |  | C-EUC1206 | C1206 | C3, C4 | CAPACITOR, European symbol
2 |  | CPOL-USE2.5-5 | E2,5-5 | C5, C6 | POLARIZED CAPACITOR, American symbol
4 |  | DIODE-SMB | SMB | D1, D2, D3, D4 | DIODE
2 |  | LEDCHIPLED_1206 | CHIPLED_1206 | LED1, LED2 | LED
1 |  | PINHD-1X1 | 1X01 | JP1 | Pin header 1x1 for 0.1 spacing"
1 |  | W237-103 | W237-103 | X5 | WAGO SCREW CLAMP
2 | 0 | R-US_R1206 | R1206 | R5, R13 | RESISTOR, American symbol
2 | 100k | R-US_R1206 | R1206 | R7, R12 | RESISTOR, American symbol
2 | 10u | C-EUC1210 | C1210 | C11, C15 | CAPACITOR, European symbol
8 | 1n | C-EUC1206 | C1206 | C2, C8, C9, C10, C12, C14, C16, C17 | CAPACITOR, European symbol
2 | 2.2k | R-US_R1206 | R1206 | R8, R9 | RESISTOR, American symbol
4 | 370u | L-USL1812 | L1812 | L1, L2, L3, L4 | INDUCTOR, American symbol
1 | 3n | C-EUC1206 | C1206 | C13 | CAPACITOR, European symbol
1 | 3u | C-EUC1206 | C1206 | C1 | CAPACITOR, European symbol
8 | 470 | R-US_R1206 | R1206 | R1, R2, R3, R4, R10, R11, R15, R16 | RESISTOR, American symbol
2 | 50n | C-EUC1210 | C1210 | C7, C18 | CAPACITOR, European symbol
4 | BU-SMA-V | BU-SMA-V | BU-SMA-V | X1, X2, X3, X4 | FEMALE SMA CONNECTOR
1 | TLV272IS-13SO8_DIO-M | TLV272IS-13SO8_DIO-M | SO8_DIO-M | U1 |  | EMA_UL_Team | TLV272IS-13 | Other opamps e.g. ADA4817 or similar will be better suited-- the footprint is generic
11 | TPTP20SQ | TPTP20SQ | TP20SQ | TP1, TP2, TP3, TP4, TP5, TP6, TP7, TP8, TP9, TP10, TP11 | Test pad
2 | open | R-US_R1206 | R1206 | R6, R14 | RESISTOR, American symbol

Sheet: Drive Amplifier
Qty | Value | Device | Package | Parts | Description | DATASHEET_URL | DESCRIPTION | FAMILY_NAME | GENERIC_PART_NUMBER | INDUSTRY_STD_PKG_TYPE | MANUFACTURER | MANUFACTURER_PART_NUMBER | MF | MPN | OC_FARNELL | OC_NEWARK | PACKAGE_DESIGNATOR | PIN_COUNT | POPULARITY | SPICEPREFIX | TP_SIGNAL_NAME | VENDOR
1 |  | LEDCHIPLED_0805 | CHIPLED_0805 | LED1 | LED |  |  |  |  |  |  |  |  |  |  |  |  |  | 52
2 |  | PINHD-1X2 | 1X02 | JP1, JP2 | PIN HEADER |  |  |  |  |  |  |  |  |  |  |  |  |  | 98
3 |  | W237-102 | W237-102 | V+TERM, VINTERM, VOUT_TERM | WAGO SCREW CLAMP |  |  |  |  |  |  |  |  | 237-102 | unknown | 70K9898 |  |  | 32
8 | .1u | C-EUC1206 | C1206 | C4, C5, C6, C7, C8, C9, C10, C11 | CAPACITOR, European symbol |  |  |  |  |  |  |  |  |  |  |  |  |  | 54 | C
1 | 0.1 | R-EU_VTA52 | VTA52 | R4 | RESISTOR, European symbol |  |  |  |  |  |  |  |  |  |  |  |  |  | 0 | R
1 | 100k | R-US_R1206 | R1206 | R12 | RESISTOR, American symbol |  |  |  |  |  |  |  |  |  |  |  |  |  | 19 | R
1 | 100p | C-EUC1206 | C1206 | C3 | CAPACITOR, European symbol |  |  |  |  |  |  |  |  |  |  |  |  |  | 54 | C
1 | 100u | C-US050-025X075 | C050-025X075 | C1 | CAPACITOR, American symbol |  |  |  |  |  |  |  |  |  |  |  |  |  | 0 | C
1 | 10V | SCHOTTKY-DIODEDO35-7 | DO35-7 | D1 | Schottky Diode
1 | 10k | R-US_R1206 | R1206 | R9 | RESISTOR, American symbol |  |  |  |  |  |  |  |  |  |  |  |  |  | 19 | R
1 | 1u | C-EUC1206 | C1206 | C2 | CAPACITOR, European symbol |  |  |  |  |  |  |  |  |  |  |  |  |  | 54 | C
9 | 2.2k | R-US_R1206 | R1206 | R1, R2, R6, R8, R10, R11, R13, R14, R15 | RESISTOR, American symbol |  |  |  |  |  |  |  |  |  |  |  |  |  | 19 | R
2 | 22k | R-US_R1206 | R1206 | R5, R7 | RESISTOR, American symbol |  |  |  |  |  |  |  |  |  |  |  |  |  | 19 | R
1 | 3V | SCHOTTKY-DIODEDO35-7 | DO35-7 | D3 | Schottky Diode
1 | 4.7k | R-US_R1206 | R1206 | R3 | RESISTOR, American symbol |  |  |  |  |  |  |  |  |  |  |  |  |  | 19 | R
1 | 78L12F | 78L12F | SOT89 | IC4 | POSITOIV-VOLTAGE REGULATORS |  |  |  |  |  |  |  |  |  |  |  |  |  | 0
1 | 7A | R-US_R1206 | R1206 | FUSE_1 | RESISTOR, American symbol |  |  |  |  |  |  |  |  |  |  |  |  |  | 19 | R
1 | INA105U | INA105U | SO08 | IC1 | Precision Unity Gain Diff. Amplifier |  |  |  |  |  |  |  | TEXAS INSTRUMENTS | INA105KU | 1754832 | 35C0475 |  |  | 0
1 | LM358MX | LM358MX | SO08 | IC2 | OP AMP also LM158, LM258, LM2904 |  |  |  |  |  |  |  |  |  |  |  |  |  | 0
1 | OPA549T | OPA549T | KV11 | U1 |  | http://www.ti.com/lit/gpn/OPA549 | High-Voltage, High-Current Op Amp, Excellent Output Swing | HIGH OUTPUT CURRENT | OPA549 | TO-220 | Texas Instruments | OPA549T |  |  |  |  | KV | 11 |  |  |  | Texas Instruments
1 | SPD30P06PTO252 | SPD30P06PTO252 | TO252 | Q1 | SIPMOS(R) Power-Transistor P-Channel, Enhancement mode |  |  |  |  |  |  |  |  |  |  |  |  |  | 3
11 | TPTP20SQ | TPTP20SQ | TP20SQ | TP1, TP2, TP3, TP4, TP5, TP6, TP7, TP8, TP9, TP10, TP11 | Test pad |  |  |  |  |  |  |  |  |  |  |  |  |  | 2

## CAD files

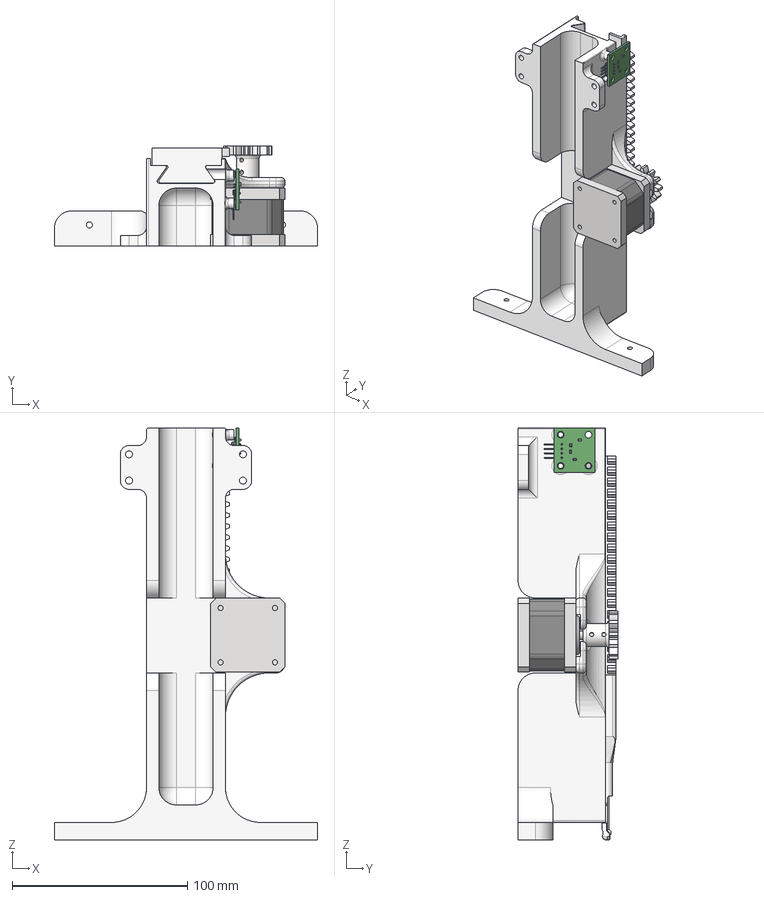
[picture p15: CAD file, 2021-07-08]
Inventor Parts/MPSV2/6xxx_Sample Assembly/6000_Sample Assembly_V2-Jul82021.stp
150.2 x 57.0 x 235.0 mm
6101_Sample Rail Base_V2
3102_Dovetail Slider_V2
3211_Stepper Motor_V1
Spur Gear1
3104_Example Bulb_V1
3103_Bulb Arm_V4
EdgeDetector

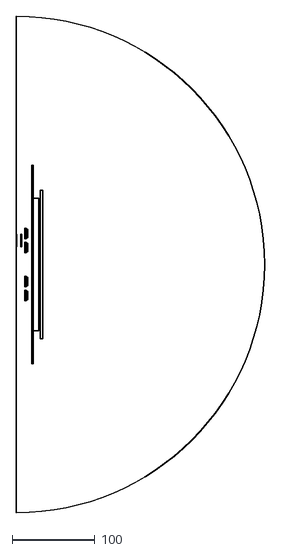
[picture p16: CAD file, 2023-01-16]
General Documentation/FEMM/DriveCoil-Litz_N22Each-20mmID.dxf
300.0 x 600.0

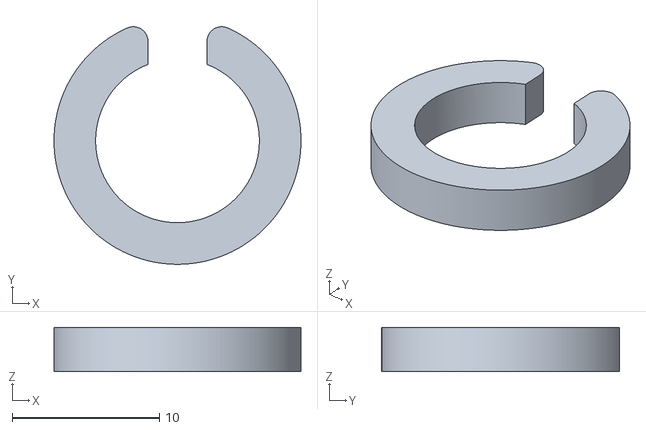
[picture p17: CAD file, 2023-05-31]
Inventor Parts/MPSV2/2xxx Coil Formers and Parts/20xx Rx Coil/200x Rx Coil Solenoid Former/2002_Rx_Tx Coil Spacer_Glass_v3.stl
16.7 x 16.1 x 3.00

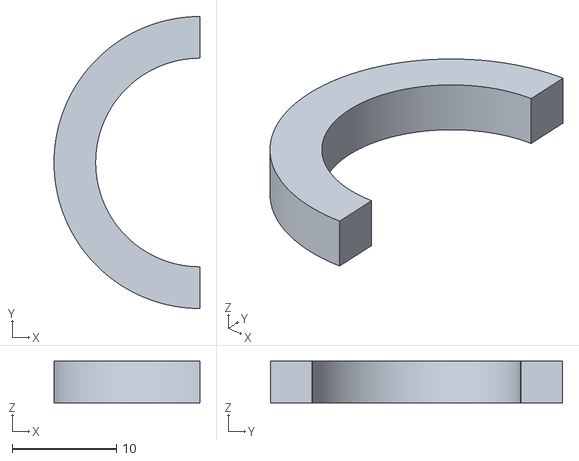
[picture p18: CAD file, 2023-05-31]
Inventor Parts/MPSV2/2xxx Coil Formers and Parts/21xx Tx Coil/210x Tx Coil Solenoid Former/2101b_Tx_Coil_Spacer_short_v1.stl
14.0 x 28.0 x 4.00

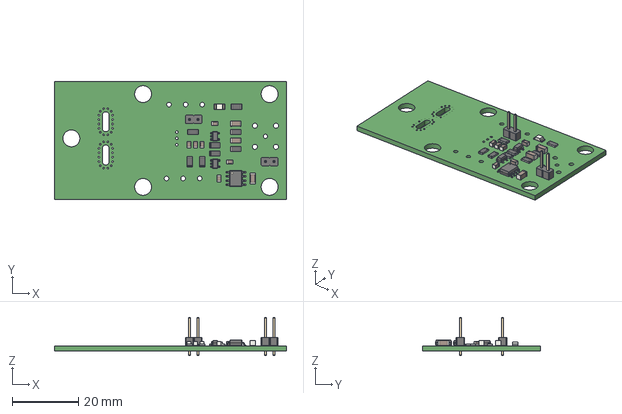
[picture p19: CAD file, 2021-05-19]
Inventor Parts/MPSV2/4xxx PCB and Filters/42xx Current Sense Circuits/ACS770_CurrentSense.step
69.8 x 35.6 x 11.5 mm

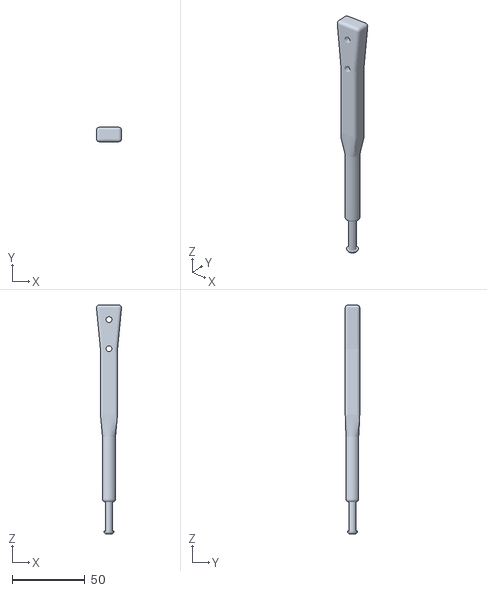
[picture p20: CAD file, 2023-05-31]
Inventor Parts/MPSV2/6xxx_Sample Assembly/61xx_Sample Rails/6103C_Bulb Arm_CalibCoil.stl
17.2 x 10.0 x 157.0

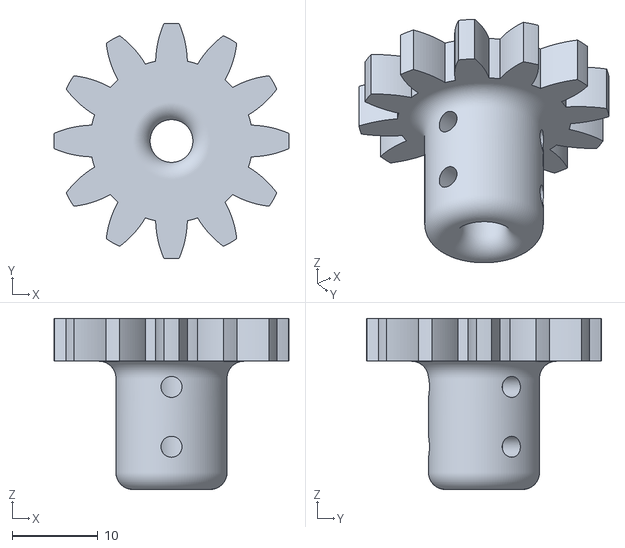
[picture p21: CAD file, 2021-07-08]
Inventor Parts/MPSV2/6xxx_Sample Assembly/62xx_ Motor and Driving/622x_Motor Mechanical Connectors/6221_Motor Pinion_V3.stl
27.5 x 27.5 x 20.0

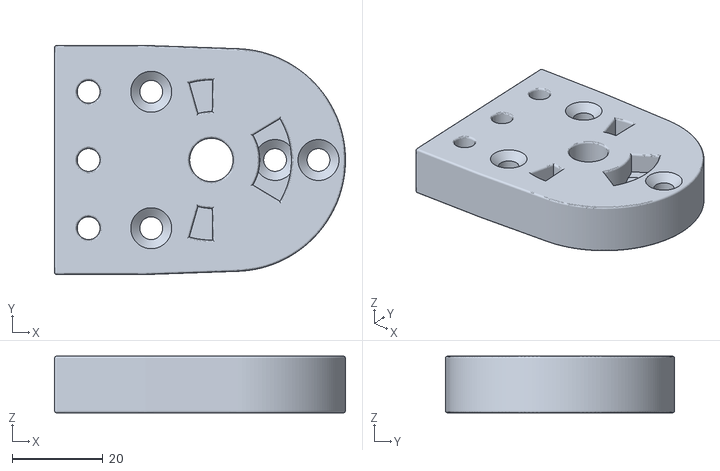
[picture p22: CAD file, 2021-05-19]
Inventor Parts/MPSV2/Final 3D Print Parts/5101_Tx_Rx_Relative_Position_Adjust_Tx_Adadpter_Female_MPSv2_v4.stl
64.0 x 50.4 x 12.5

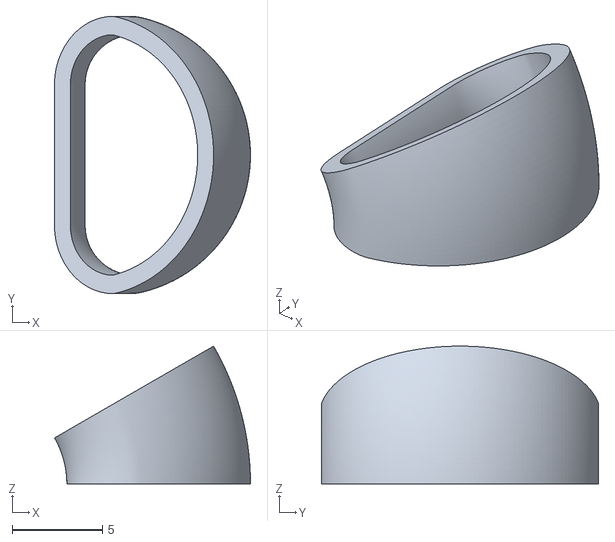
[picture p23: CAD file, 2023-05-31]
Inventor Parts/MPSV2/Tx_Filter_Toroids/L_20uH-Wedge.stl
10.9 x 15.4 x 7.65

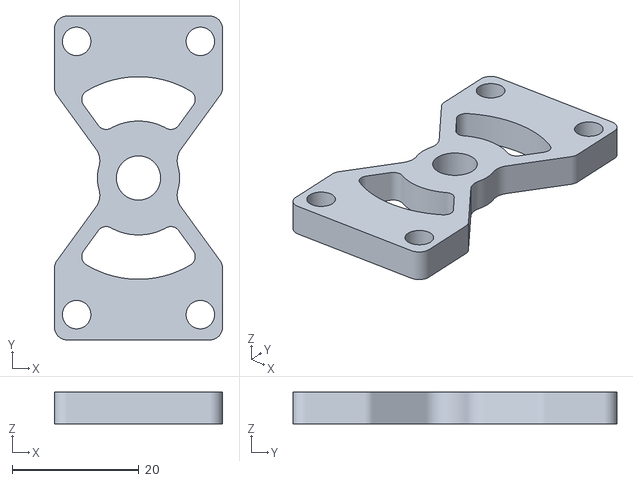
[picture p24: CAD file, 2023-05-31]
Inventor Parts/MPSV2/2xxx Coil Formers and Parts/21xx Tx Coil/210x Tx Coil Solenoid Former/2104_Tx_CoilBackPlate_V1.stl
26.6 x 51.2 x 5.00

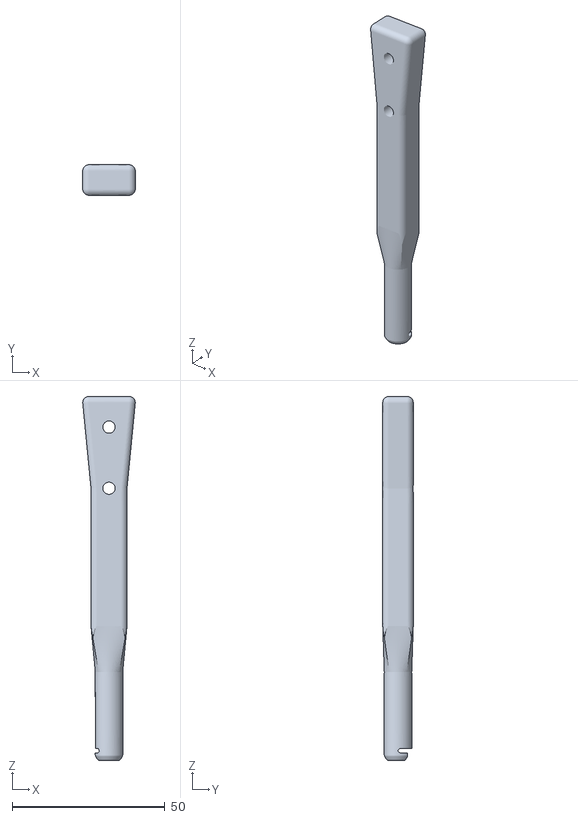
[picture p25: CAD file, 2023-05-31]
Inventor Parts/MPSV2/6xxx_Sample Assembly/61xx_Sample Rails/6103B_Bulb Arm_Microcentrifuge-tube-0,2mL_V2.stl
17.2 x 10.0 x 119.0

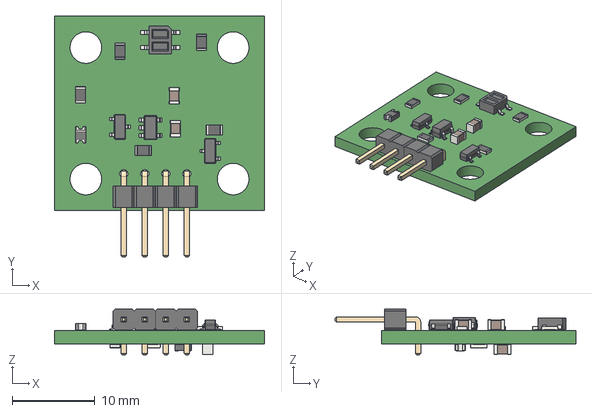
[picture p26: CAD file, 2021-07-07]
Inventor Parts/MPSV2/6xxx_Sample Assembly/EdgeDetector.step
25.4 x 29.1 x 5.54 mm

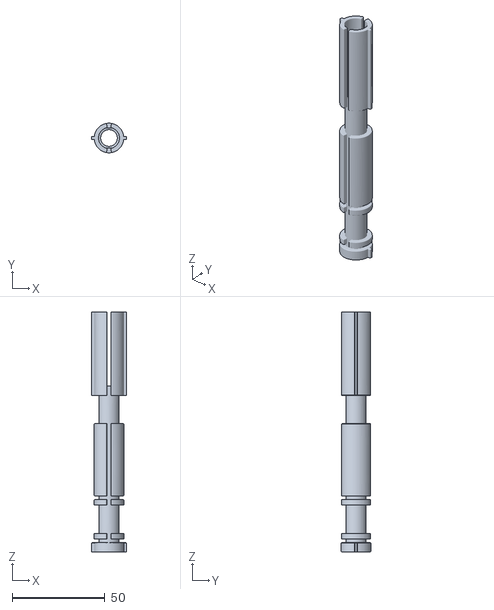
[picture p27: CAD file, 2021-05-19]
Inventor Parts/MPSV2/Final 3D Print Parts/2000_Rx_Coil_Holder_MPSv2_v2.stl
18.9 x 16.0 x 129.6

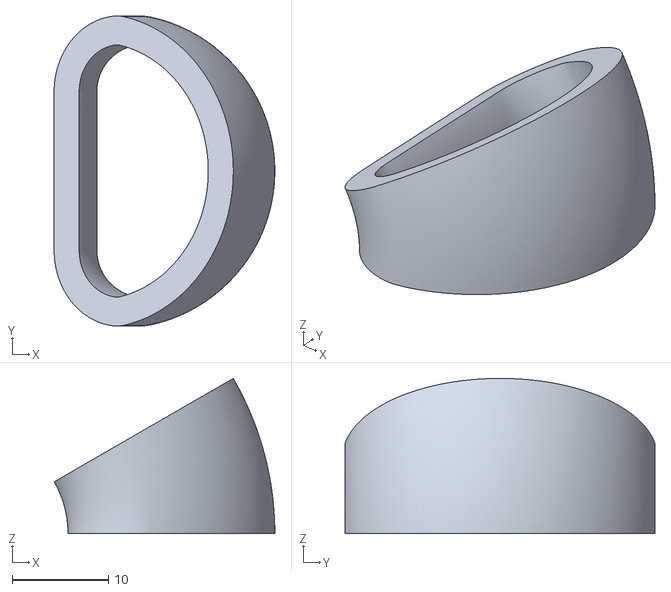
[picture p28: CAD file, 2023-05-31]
Inventor Parts/MPSV2/Tx_Filter_Toroids/L_Notch1-Wedge.stl
22.9 x 32.2 x 16.1

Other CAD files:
Inventor Parts/MPSV2/1221_Backside Angle Bracket_V5.dwg
Inventor Parts/MPSV2/2xxx Coil Formers and Parts/21xx Tx Coil/210x Tx Coil Solenoid Former/2103_Tx_CoilFin_Spacer_V1.stl
Inventor Parts/MPSV2/6xxx_Sample Assembly/61xx_Sample Rails/6103B_Bulb Arm_Microcentrifuge-tube-0,2mL.stl
Inventor Parts/MPSV2/Tx_Filter_Toroids/L_Filt1-Wedge.stl
Inventor Parts/Archive/Version 1/1xxx_Transmit Assembly/13xx_Drive Coil/1310_Drive Coil Assm_V2.iam
Inventor Parts/Archive/Version 1/1xxx_Transmit Assembly/13xx_Drive Coil/1311_Drive Coil Main Body_V2.ipt
Inventor Parts/Archive/Version 1/1xxx_Transmit Assembly/13xx_Drive Coil/1313_Drive Coil End_V2.ipt
Inventor Parts/Archive/Version 1/1xxx_Transmit Assembly/13xx_Drive Coil/1313_Drive Coil End_V2_TMP.ipt
Inventor Parts/Archive/Version 1/1xxx_Transmit Assembly/13xx_Drive Coil/1314_Drive Tuning Nut Holder_V1.ipt
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

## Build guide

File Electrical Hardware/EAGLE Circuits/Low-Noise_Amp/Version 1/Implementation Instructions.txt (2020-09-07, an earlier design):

This circuit has not been implemented yet (albeit a similar version has utilizing only the INA217), and therefore it should not be considered a final product. Further, it was designed to allow flexibility in its applications, and as a result care must be taken to configure it properly. A number of the 0Ohm resistors are designed to act as semi-permanent switches to allow configuration. 

To use the amplifier in the simplest mode (and most similar to the currently working circuit) the following 0 Ohm resistors should be shorted. ALL OTHERS SHOULD BE LEFT OPEN.

R9
R10
R27
R26

In this arrangement it has been tested and works well. I would not reccomend using the optional JFETs-- they were included on the board for experimentation, but do not help. 

The value for R4 is flexible, but should be a high quality resistor (e.g. not carbon. Wirewound should be good), but it should be at least 20 Ohms to ensure amplifier stability. C5 also is flexible in terms of value, and just serves to bandwidth limit the amplifier to ~1MHz. 

R1,5,6,7 are available for the end-user to pick the values based on what gain you want. See the datasheet for the INA217 for the gain calculation.

The second half of this circuit (based on LT1115) is still under development/testing.

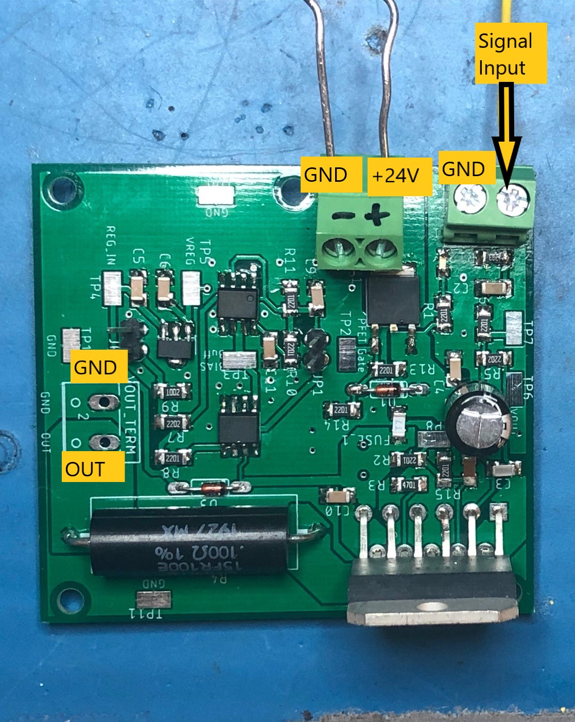
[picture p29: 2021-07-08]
Electrical Hardware/Setup and Testing/Drive Amp Picture_Label.jpg

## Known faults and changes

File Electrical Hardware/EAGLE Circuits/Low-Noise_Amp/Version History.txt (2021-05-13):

Version 1 was a trial board that included many options for experimentation using either the INA217 or the LT1115. The INA217 had better performance, but in order to work well, a few changes needed to be made. Mainly, we added resistors to ground (~2.2k) from both of the input terminals to remove the DC offset which occurs if there is no DC path to ground

Version 2 removes unnecessary components and simplifies the design.

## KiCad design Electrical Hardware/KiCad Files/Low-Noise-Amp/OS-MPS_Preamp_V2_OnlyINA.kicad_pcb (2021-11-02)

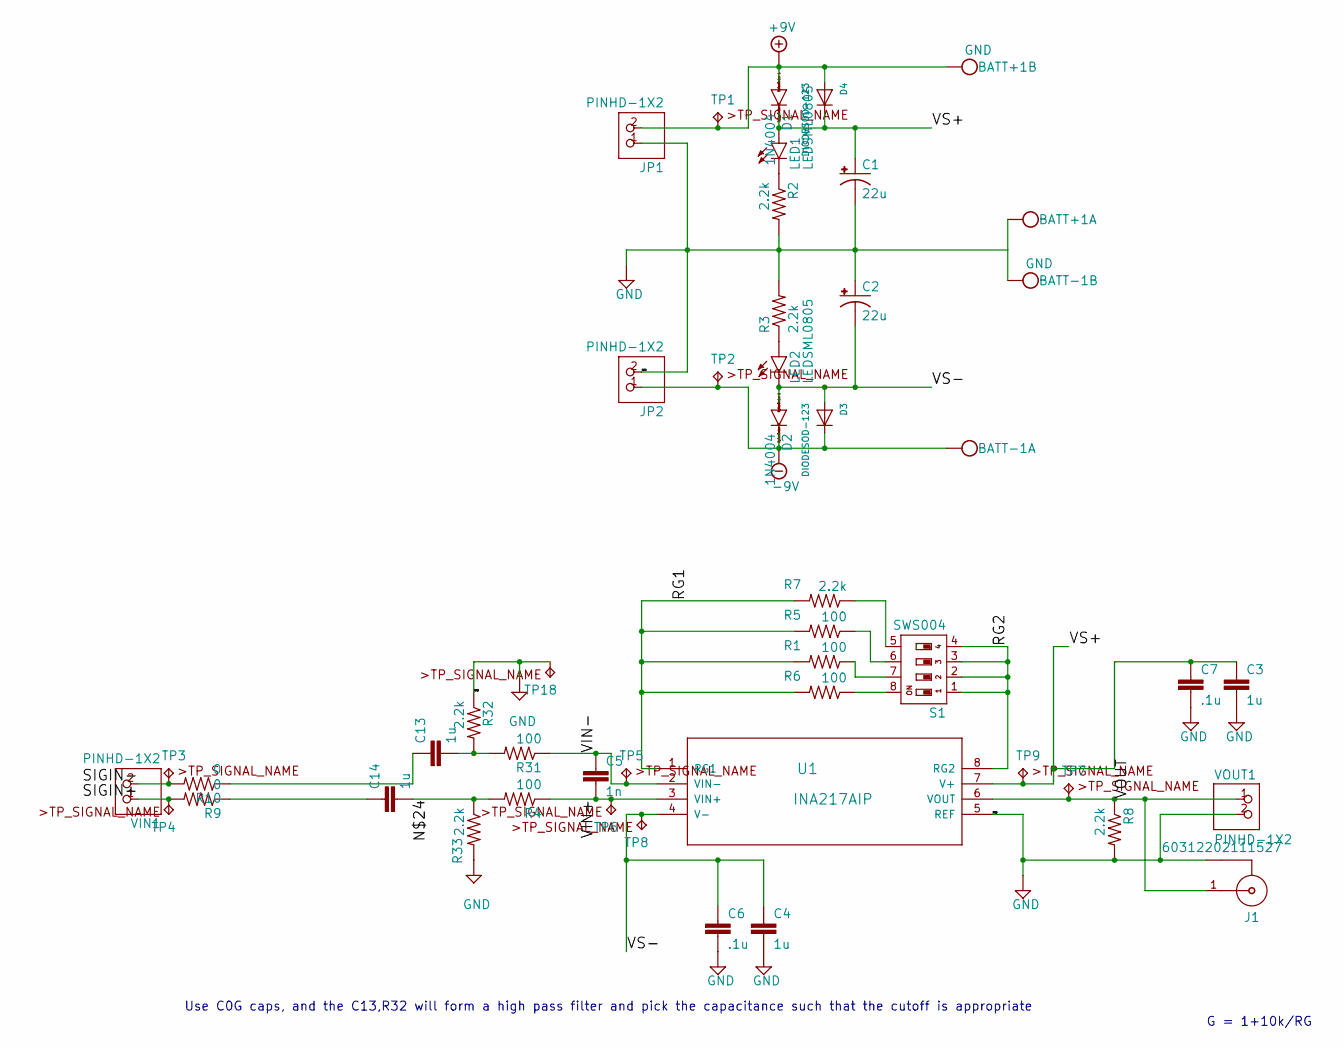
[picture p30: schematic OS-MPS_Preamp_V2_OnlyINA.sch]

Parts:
BATT+1: GND; W237-102
BATT-1: GND; W237-102
C1, C2: 22u; TT2D6
C3, C4, C13, C14: 1u; C1206
C5: 1n; C1206
C6, C7: .1u; C1206
D1, D2: 1N4004; DO41-10
D3, D4: DIODESOD-123; SOD-123
J1: 60312202111527
JP1, JP2: PINHD-1X2; 1X02
LED1, LED2: LEDSML0805; SML0805
R1, R4, R5, R6, R31: 100; R0805
R2, R3, R7, R8, R32, R33: 2.2k; R0805
R9, R10: 0; R0805
S1: SWS004; SMS-004
TP1, TP2: TPB2,54; B2,54
TP3, TP4, TP5, TP6, TP7, TP8, TP9, TP18: TPTP20SQ; TP20SQ
U1: INA217AIP; P8
VIN1: PINHD-1X2; 1X02
VOUT1: PINHD-1X2; 1X02

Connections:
+9V: BATT+1.2, D1.A, D4.A, JP1.2, TP1.TP
-9V: BATT-1.1, D2.C, D3.C, JP2.1, TP2.TP
/N$24: C14.2, R4.2, R33.1
/RG1: R1.2, R5.2, R6.2, R7.2, U1.1 (RG1)
/RG2: S1.1, S1.2, S1.3, S1.4, U1.8 (RG2)
/SIGIN+: R9.2, TP4.TP, VIN1.1
/SIGIN-: R10.2, TP3.TP, VIN1.2
/VIN+: C5.2, R4.1, TP6.TP, U1.3 (VIN+)
/VIN-: C5.1, R31.1, TP5.TP, U1.2 (VIN-)
/VOUT: J1.1, R8.1, TP7.TP, U1.6 (VOUT), VOUT1.1
/VS+: C1.+, C3.1, C7.1, D1.C, D4.C, LED1.A, TP9.TP, U1.7 (V+)
/VS-: C2.-, C4.1, C6.1, D2.A, D3.A, LED2.C, TP8.TP, U1.4 (V-)
GND: BATT+1.1, BATT-1.2, C1.-, C2.+, C3.2, C4.2, C6.2, C7.2, J1.2, J1.3 (2), J1.4 (2), J1.5 (2), JP1.1, JP2.2, R2.2, R3.2, R8.2, R32.1, R33.2, TP18.TP, U1.5 (REF), VOUT1.2
unnamed: C13.1, R10.1
unnamed: C13.2, R31.2, R32.2
unnamed: C14.1, R9.1
unnamed: LED1.C, R2.1
unnamed: LED2.A, R3.1
unnamed: R1.1, S1.7
unnamed: R5.1, S1.6
unnamed: R6.1, S1.8
unnamed: R7.1, S1.5

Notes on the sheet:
Use C0G caps, and the C13,R32 will form a high pass filter and pick the capacitance such that the cutoff is appropriate
G = 1+10k/RG

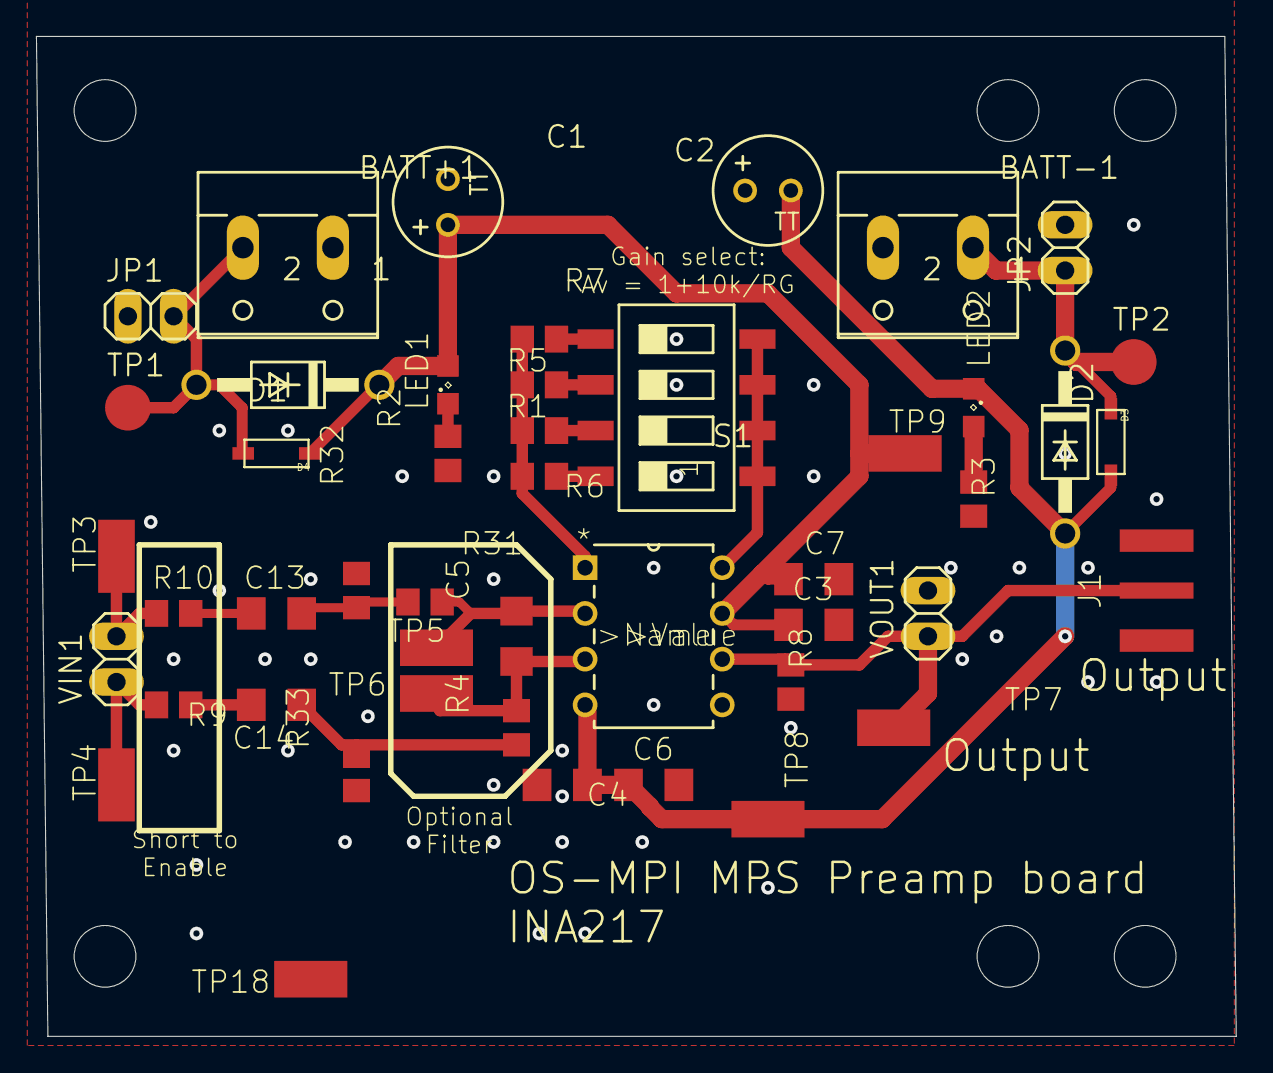
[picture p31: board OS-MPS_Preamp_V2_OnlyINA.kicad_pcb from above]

Board: 2 copper layers, 66.7 x 55.6 mm, 53 parts (0 on the bottom side), 22 nets.

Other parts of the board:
@HOLE0, @HOLE1, @HOLE2, @HOLE3, @HOLE4, @HOLE5: (no value)

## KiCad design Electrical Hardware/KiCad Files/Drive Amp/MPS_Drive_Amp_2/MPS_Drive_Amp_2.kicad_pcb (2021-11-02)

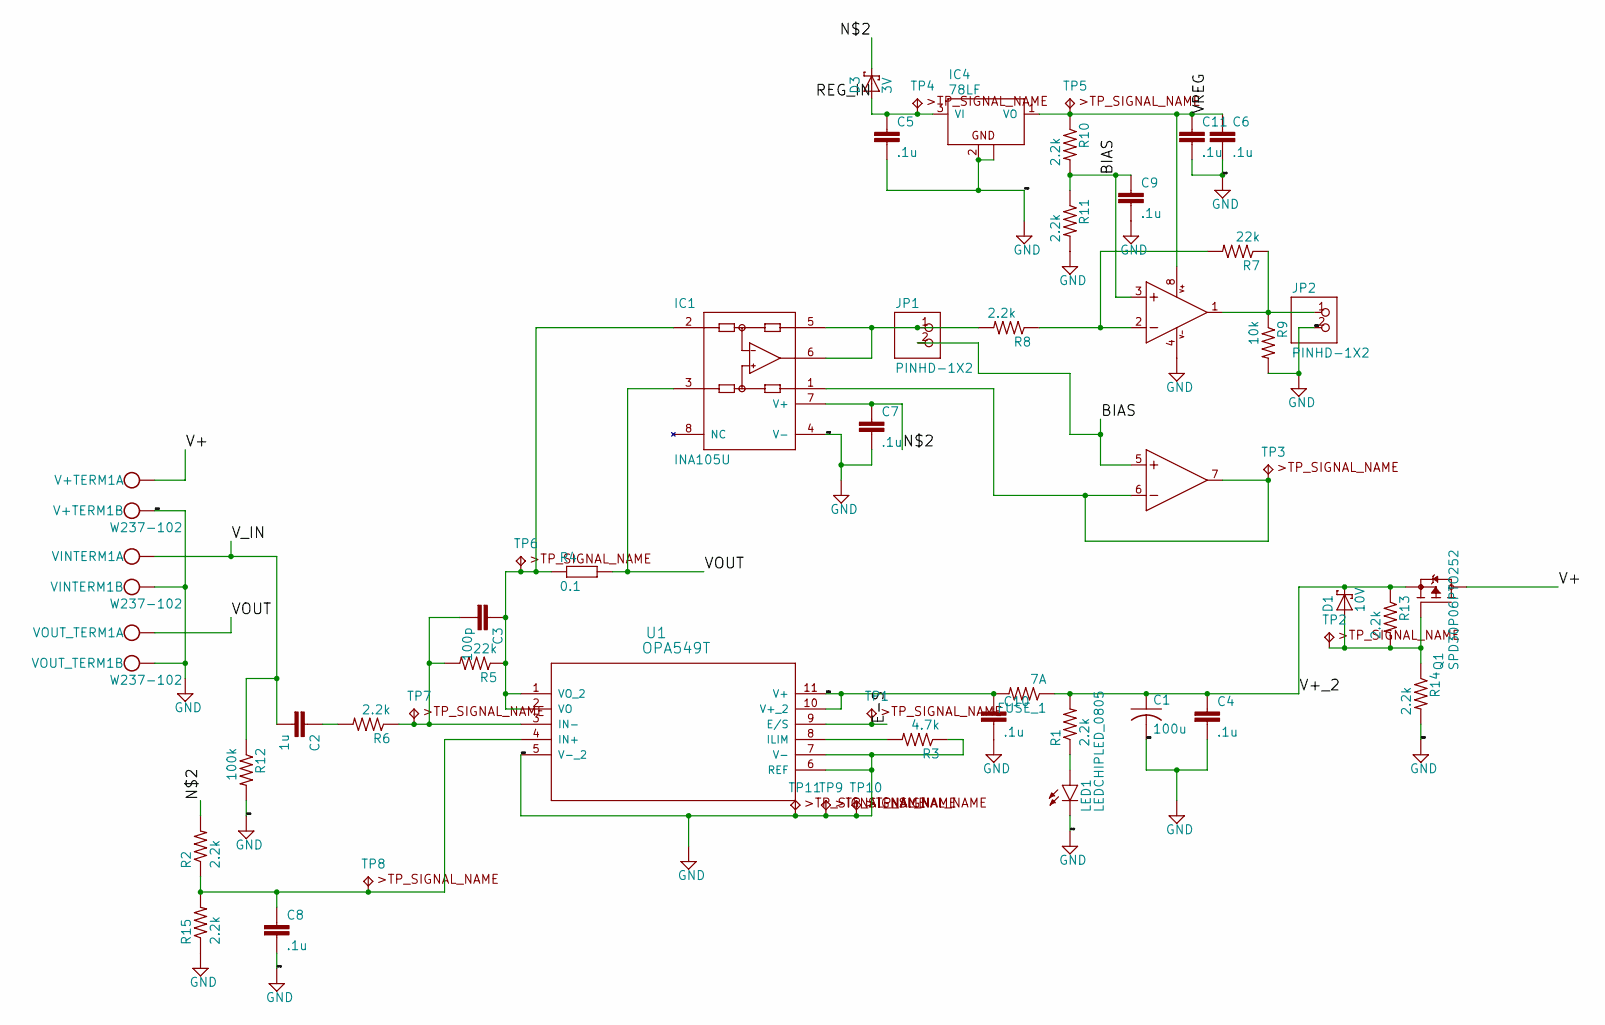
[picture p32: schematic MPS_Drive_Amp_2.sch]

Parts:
C1: 100u; C050-025X075
C2: 1u; C1206
C3: 100p; C1206
C4, C5, C6, C7, C8, C9, C10, C11: .1u; C1206
D1: 10V; DO35-7
D3: 3V; DO35-7
FUSE_1: 7A; R1206
IC1: INA105U; SO08
IC2: LM358MX; SO08
IC4: 78LF; SOT89
JP1, JP2: PINHD-1X2; 1X02
LED1: LEDCHIPLED_0805; CHIPLED_0805
Q1: SPD30P06PTO252; TO252
R1, R2, R6, R8, R10, R11, R13, R14, R15: 2.2k; R1206
R3: 4.7k; R1206
R4: 0.1; VTA52
R5, R7: 22k; R1206
R9: 10k; R1206
R12: 100k; R1206
TP1, TP2, TP3, TP4, TP5, TP6, TP7, TP8, TP9, TP10, TP11: TPTP20SQ; TP20SQ
U1: OPA549T; KV11
V+TERM1: W237-102
VINTERM1: W237-102
VOUT_TERM1: W237-102

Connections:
/BIAS: C9.1, IC2.3 (+IN), IC2.5 (+IN), JP1.2, R10.2, R11.1
/E-S: TP1.TP, U1.9 (E/S)
/N$2: C7.1, C10.1, D3.C, FUSE_1.2, IC1.7 (V+), R2.2, U1.10 (V+_2), U1.11 (V+)
/REG_IN: C5.1, D3.A, IC4.3 (VI), TP4.TP
/V+: Q1.3 (D), V+TERM1.1
/V+_2: C1.1, C4.1, D1.C, FUSE_1.1, Q1.2 (S), R1.2, R13.1
/VOUT: IC1.3 (+IN), R4.2, VOUT_TERM1.1
/VREG: C6.1, C11.1, IC2.8 (V+), IC4.1 (VO), R10.1, TP5.TP
/V_IN: C2.2, R12.1, VINTERM1.1
GND: C1.2, C4.2, C5.2, C6.2, C7.2, C8.2, C9.2, C10.2, C11.2, IC1.4 (V-), IC2.4 (V-), IC4.2 (GND), IC4.2@1 (GND@1), JP2.2, LED1.C, R3.1, R9.2, R11.2, R12.2, R14.2, R15.1, TP9.TP, TP10.TP, TP11.TP, U1.5 (V-_2), U1.6 (REF), U1.7 (V-), V+TERM1.2, VINTERM1.2, VOUT_TERM1.2
unnamed: C2.1, R6.2
unnamed: C3.1, IC1.2 (-IN), R4.1, R5.1, TP6.TP, U1.1 (VO_2), U1.2 (VO)
unnamed: C3.2, R5.2, R6.1, TP7.TP, U1.3 (IN-)
unnamed: C8.1, R2.1, R15.2, TP8.TP, U1.4 (IN+)
unnamed: D1.A, Q1.1 (G), R13.2, R14.1, TP2.TP
unnamed: IC1.1 (REF), IC2.6 (-IN), IC2.7 (OUT), TP3.TP
unnamed: IC1.5 (SENSE), IC1.6 (OUT), JP1.1, R8.2
unnamed: IC2.1 (OUT), JP2.1, R7.1, R9.1
unnamed: IC2.2 (-IN), R7.2, R8.1
unnamed: LED1.A, R1.1
unnamed: R3.2, U1.8 (ILIM)

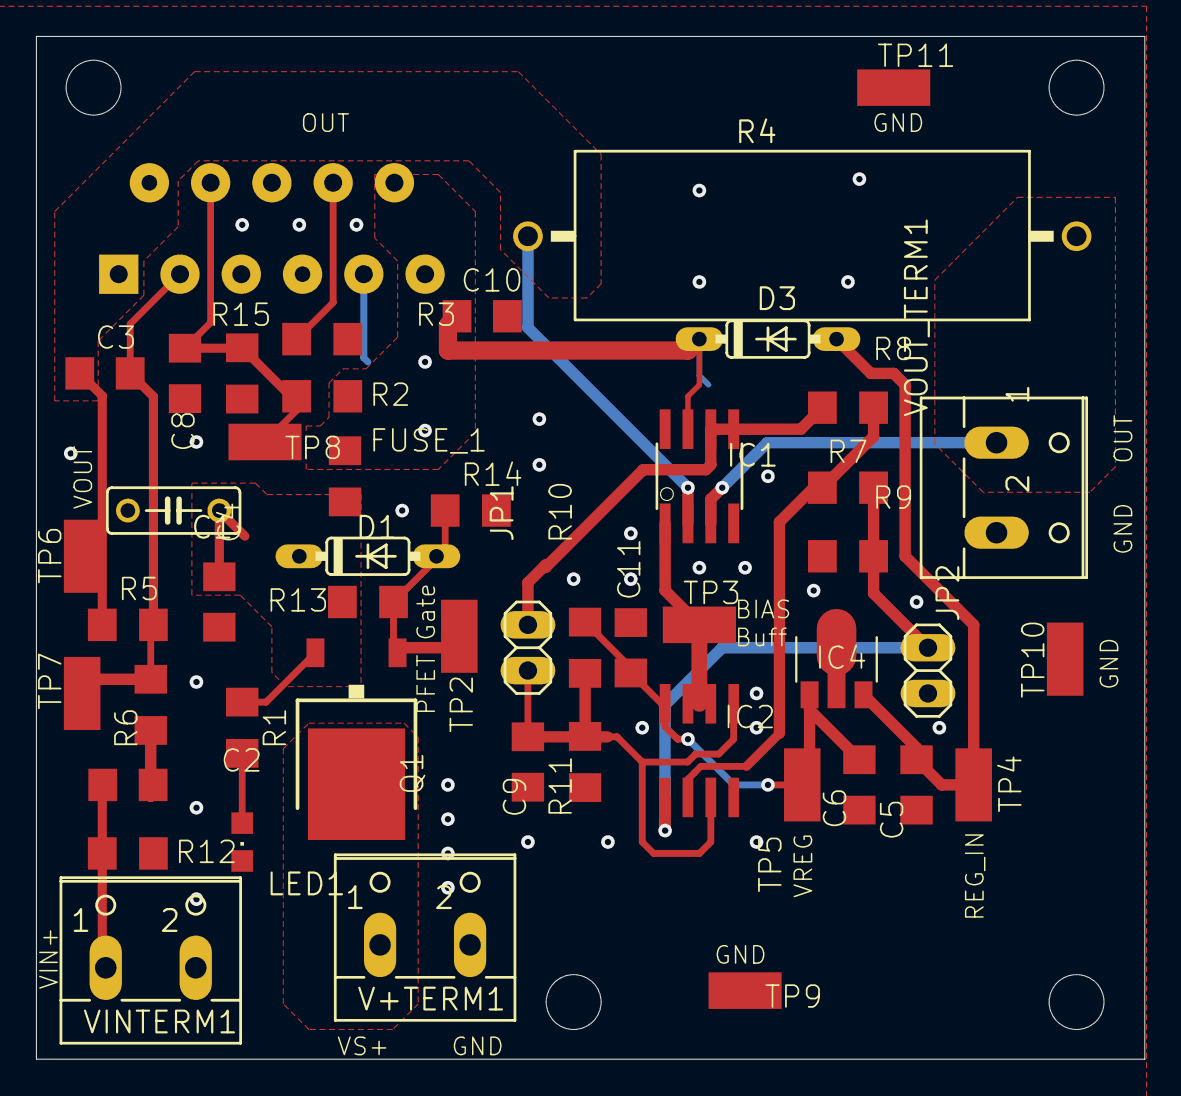
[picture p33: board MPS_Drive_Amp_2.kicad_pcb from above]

Board: 2 copper layers, 61.6 x 56.8 mm, 55 parts (0 on the bottom side), 21 nets.

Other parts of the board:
@HOLE0, @HOLE1, @HOLE2, @HOLE3: (no value)

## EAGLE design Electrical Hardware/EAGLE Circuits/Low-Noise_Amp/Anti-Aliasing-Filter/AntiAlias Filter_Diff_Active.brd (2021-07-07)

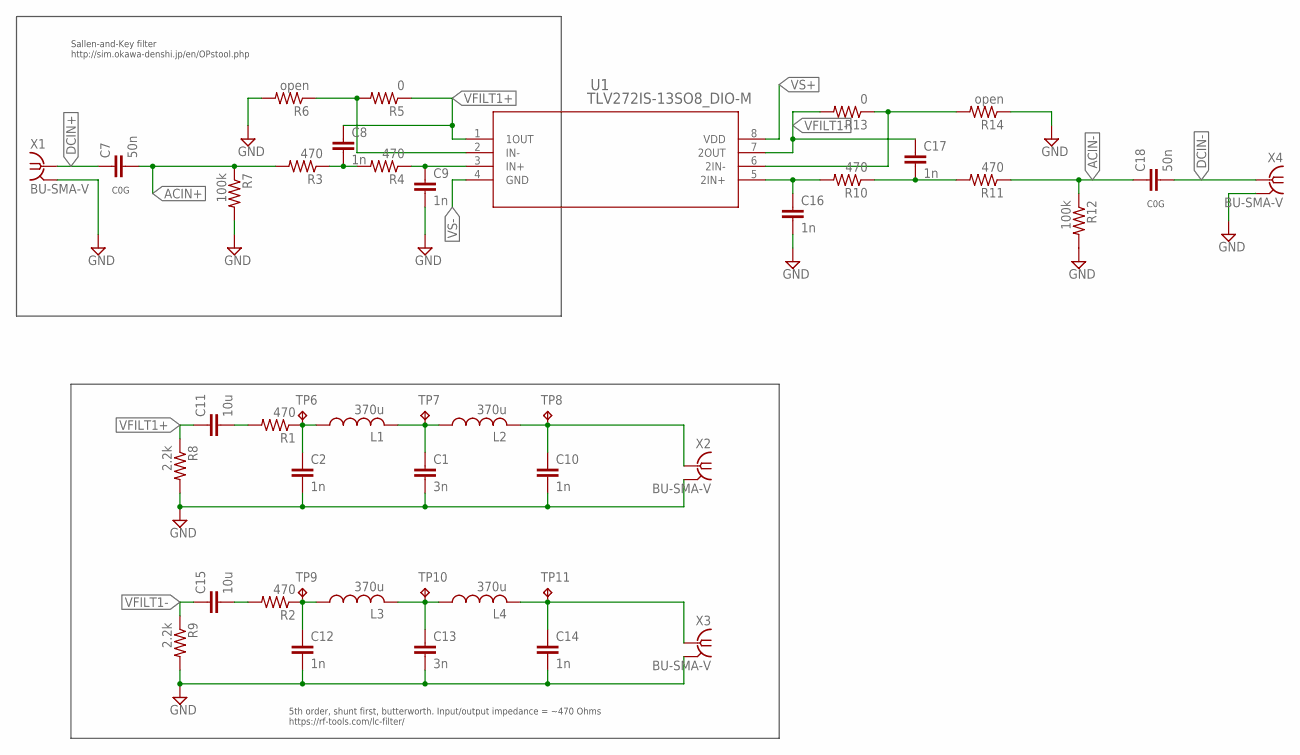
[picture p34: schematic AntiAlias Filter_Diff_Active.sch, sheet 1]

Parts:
C1, C13: 3n; C1206
C2, C8, C9, C10, C12, C14, C16, C17: 1n; C1206
C7, C18: 50n; C1210
C11, C15: 10u; C1210
L1, L2, L3, L4: 370u; L1812
R1, R2, R3, R4, R10, R11: 470; R1206
R5, R13: 0; R1206
R6, R14: open; R1206
R7, R12: 100k; R1206
R8, R9: 2.2k; R1206
TP6, TP7, TP8, TP9, TP10, TP11: TPTP20SQ; TP20SQ
U1: TLV272IS-13SO8_DIO-M; SO8_DIO-M
X1, X2, X3, X4: BU-SMA-V

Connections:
ACIN+: C7.2, R3.2, R7.1
ACIN-: C18.1, R11.1, R12.1
DCIN+: C7.1, X1.1
DCIN-: C18.2, X4.1
GND: C1.2, C2.2, C9.2, C10.2, C12.2, C13.2, C14.2, C16.2, R6.2, R7.2, R8.2, R9.2, R12.2, R14.1, X1.2, X1.3 (2), X1.4 (2), X1.5 (2), X2.2, X2.3 (2), X2.4 (2), X2.5 (2), X3.2, X3.3 (2), X3.4 (2), X3.5 (2), X4.2, X4.3 (2), X4.4 (2), X4.5 (2); also elsewhere on the board
unnamed: C2.1, L1.1, R1.1, TP6.TP
unnamed: C1.1, L1.2, L2.1, TP7.TP
unnamed: C11.2, R1.2
unnamed: C10.1, L2.2, TP8.TP, X2.1
unnamed: C14.1, L4.2, TP11.TP, X3.1
unnamed: C9.1, R4.1, U1.3 (IN+)
unnamed: C8.2, R3.1, R4.2
unnamed: R5.2, R6.1, U1.2 (IN-)
unnamed: C12.1, L3.1, R2.1, TP9.TP
unnamed: C13.1, L3.2, L4.1, TP10.TP
unnamed: C15.2, R2.2
unnamed: C17.2, R10.1, R11.2
unnamed: C16.1, R10.2, U1.5 (2IN+)
unnamed: R13.1, R14.2, U1.6 (2IN-)
VFILT1+: C8.1, C11.1, R5.1, R8.1, U1.1 (1OUT)
VFILT1-: C15.1, C17.1, R9.1, R13.2, U1.7 (2OUT)
VS+: U1.8 (VDD); also elsewhere on the board
VS-: U1.4 (GND); also elsewhere on the board

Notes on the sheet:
5th order, shunt first, butterworth. Input/output impedance = ~470 Ohms https://rf-tools.com/lc-filter/
Sallen-and-Key filter http://sim.okawa-denshi.jp/en/OPstool.php
C0G

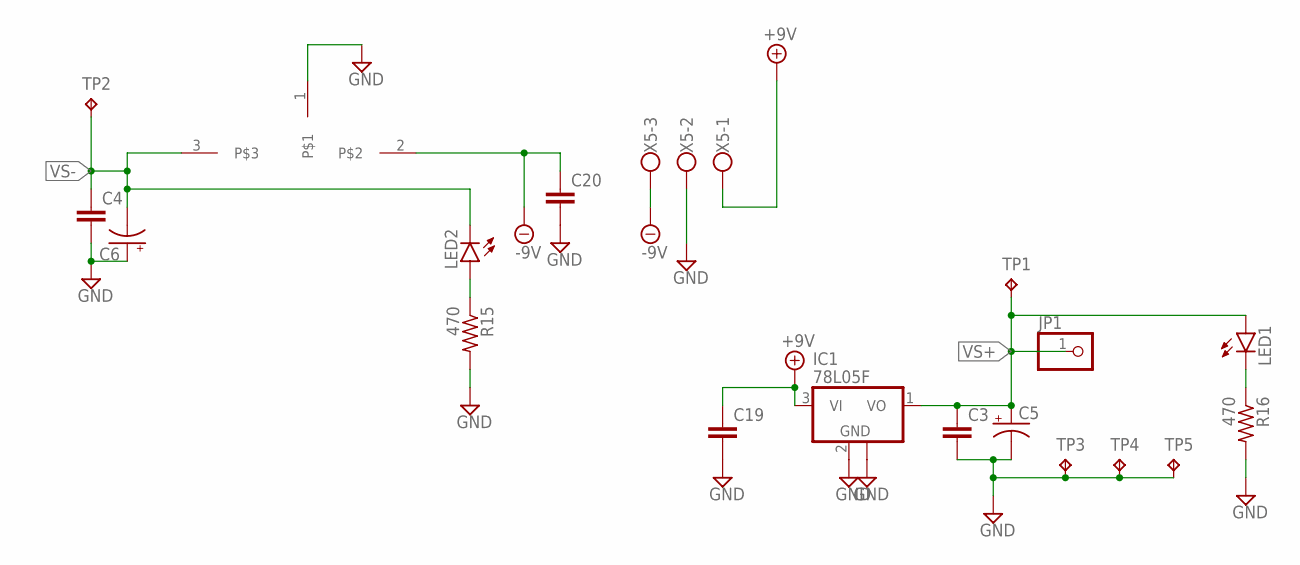
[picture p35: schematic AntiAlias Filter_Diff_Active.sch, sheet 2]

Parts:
C3, C4, C19, C20: C-EUC1206; C1206
C5, C6: CPOL-USE2.5-5; E2,5-5
IC1: 78L05F; SOT89
JP1: PINHD-1X1; 1X01
LED1, LED2: LEDCHIPLED_1206; CHIPLED_1206
R15, R16: 470; R1206
TP1, TP2, TP3, TP4, TP5: TPTP20SQ; TP20SQ
U$1: 79LXX; VREG_L78L12ABUTR
X5: W237-103

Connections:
+9V: C19.1, IC1.3 (VI), X5.1
-9V: C20.1, U$1.2, X5.3
GND: C3.2, C4.2, C5.-, C6.+, C19.2, C20.2, IC1.2 (GND), IC1.2@1 (GND), R15.2, R16.2, TP3.TP, TP4.TP, TP5.TP, U$1.1, X5.2; also elsewhere on the board
unnamed: LED2.A, R15.1
unnamed: LED1.C, R16.1
VS+: C3.1, C5.+, IC1.1 (VO), JP1.1, LED1.A, TP1.TP; also elsewhere on the board
VS-: C4.1, C6.-, LED2.C, TP2.TP, U$1.3; also elsewhere on the board

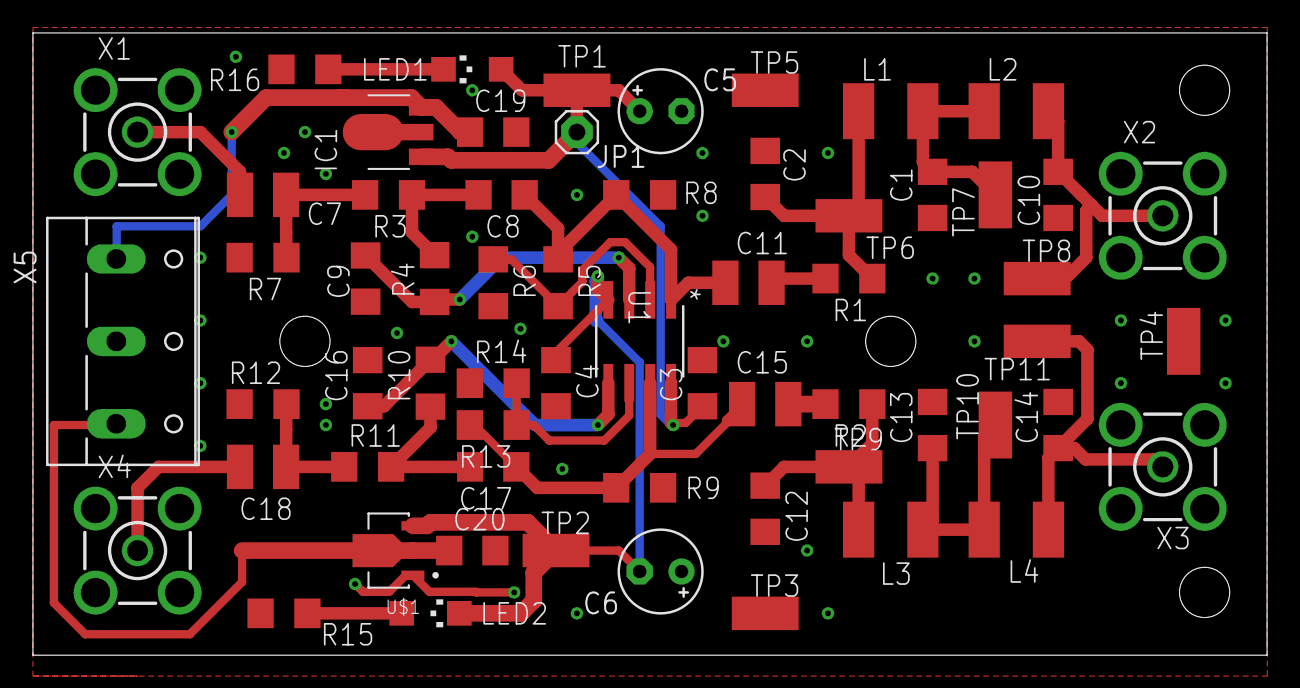
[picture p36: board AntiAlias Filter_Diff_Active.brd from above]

Board: 2 copper layers, 74.9 x 37.8 mm, 62 parts (0 on the bottom side), 27 nets.

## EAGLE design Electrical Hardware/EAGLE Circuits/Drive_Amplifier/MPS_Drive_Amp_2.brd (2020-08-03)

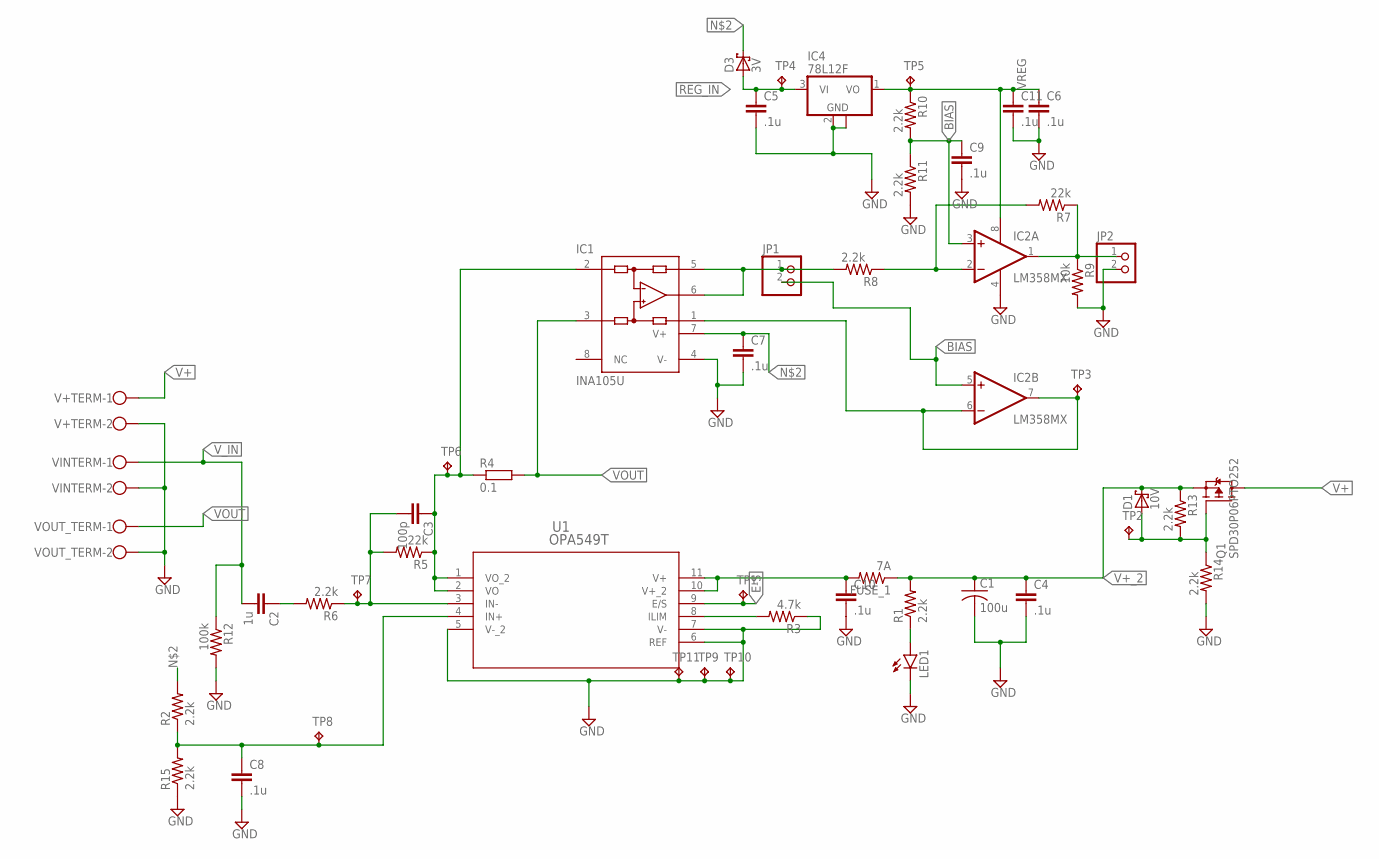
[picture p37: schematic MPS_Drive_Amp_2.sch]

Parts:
C1: 100u; C050-025X075
C2: 1u; C1206
C3: 100p; C1206
C4, C5, C6, C7, C8, C9, C10, C11: .1u; C1206
D1: 10V; DO35-7
D3: 3V; DO35-7
FUSE_1: 7A; R1206
IC1: INA105U; SO08
IC2: LM358MX; SO08
IC4: 78L12F; SOT89
JP1, JP2: PINHD-1X2; 1X02
LED1: LEDCHIPLED_0805; CHIPLED_0805
Q1: SPD30P06PTO252; TO252
R1, R2, R6, R8, R10, R11, R13, R14, R15: 2.2k; R1206
R3: 4.7k; R1206
R4: 0.1; VTA52
R5, R7: 22k; R1206
R9: 10k; R1206
R12: 100k; R1206
TP1, TP2, TP3, TP4, TP5, TP6, TP7, TP8, TP9, TP10, TP11: TPTP20SQ; TP20SQ
U1: OPA549T; KV11
V+TERM: W237-102
VINTERM: W237-102
VOUT_TERM: W237-102

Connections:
BIAS: C9.1, IC2.3 (+IN), IC2.5 (+IN), JP1.2, R10.2, R11.1
E-S: TP1.TP, U1.9 (E/S)
GND: C1.2, C4.2, C5.2, C6.2, C7.2, C8.2, C9.2, C10.2, C11.2, IC1.4 (V-), IC2.4 (V-), IC4.2 (GND), IC4.2@1 (GND), JP2.2, LED1.C, R3.1, R9.2, R11.2, R12.2, R14.2, R15.1, TP9.TP, TP10.TP, TP11.TP, U1.5 (V-_2), U1.6 (REF), U1.7 (V-), V+TERM.2, VINTERM.2, VOUT_TERM.2
unnamed: C3.1, IC1.2 (-IN), R4.1, R5.1, TP6.TP, U1.1 (VO_2), U1.2 (VO)
unnamed: C7.1, C10.1, D3.C, FUSE_1.2, IC1.7 (V+), R2.2, U1.10 (V+_2), U1.11 (V+)
unnamed: R3.2, U1.8 (ILIM)
unnamed: C2.1, R6.2
unnamed: LED1.A, R1.1
unnamed: C3.2, R5.2, R6.1, TP7.TP, U1.3 (IN-)
unnamed: IC1.5 (SENSE), IC1.6 (OUT), JP1.1, R8.2
unnamed: IC1.1 (REF), IC2.6 (-IN), IC2.7 (OUT), TP3.TP
unnamed: IC2.1 (OUT), JP2.1, R7.1, R9.1
unnamed: C8.1, R2.1, R15.2, TP8.TP, U1.4 (IN+)
unnamed: IC2.2 (-IN), R7.2, R8.1
PFET_GT: D1.A, Q1.1 (G), R13.2, R14.1, TP2.TP
REG_IN: C5.1, D3.A, IC4.3 (VI), TP4.TP
V+: Q1.3 (D), V+TERM.1
V+_2: C1.1, C4.1, D1.C, FUSE_1.1, Q1.2 (S), R1.2, R13.1
VOUT: IC1.3 (+IN), R4.2, VOUT_TERM.1
VREG: C6.1, C11.1, IC2.8 (V+), IC4.1 (VO), R10.1, TP5.TP
V_IN: C2.2, R12.1, VINTERM.1

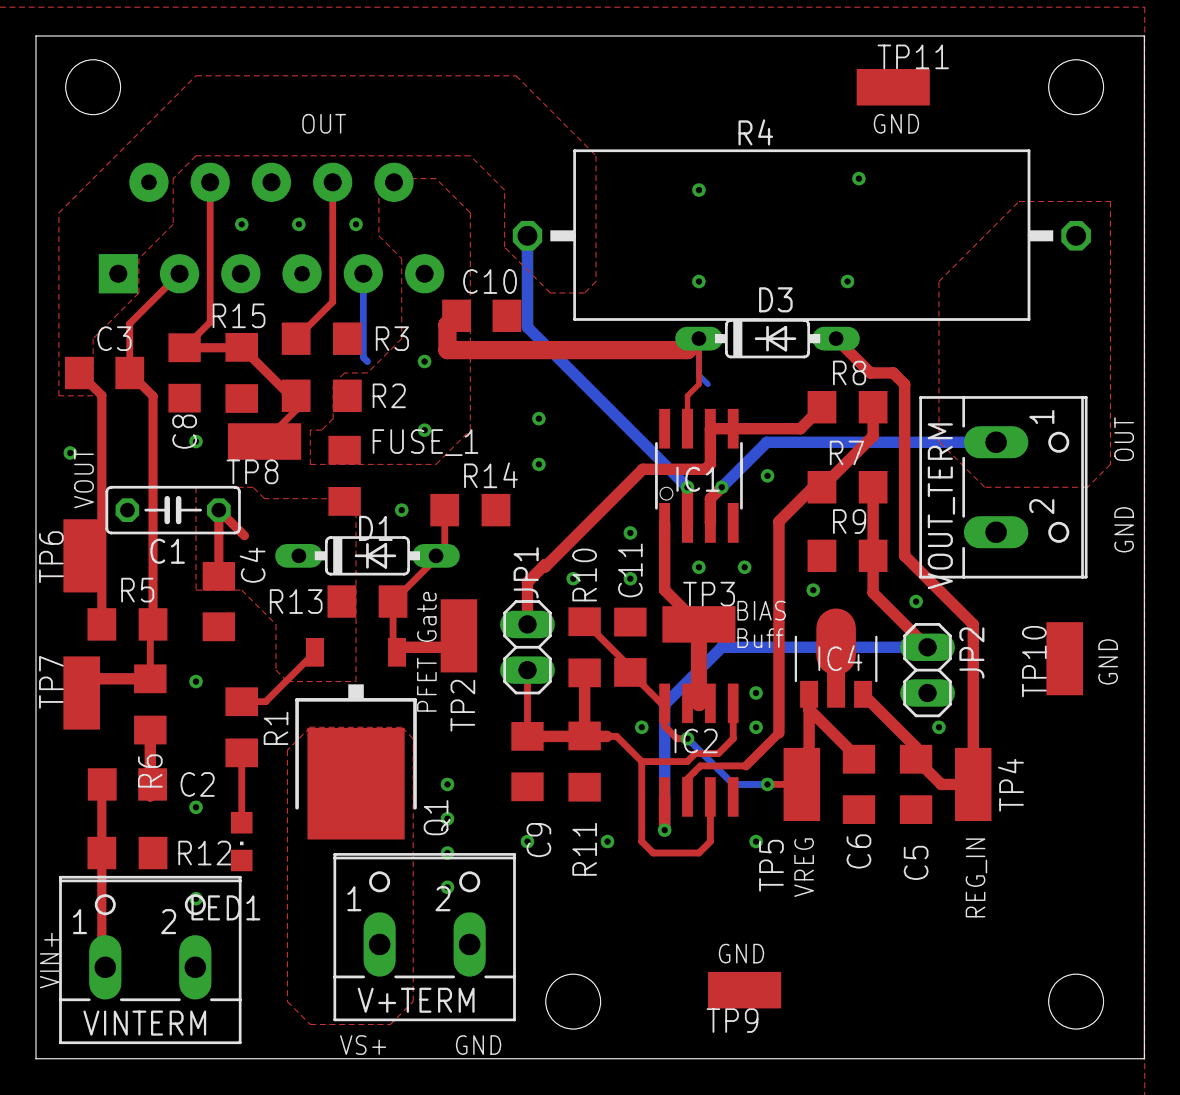
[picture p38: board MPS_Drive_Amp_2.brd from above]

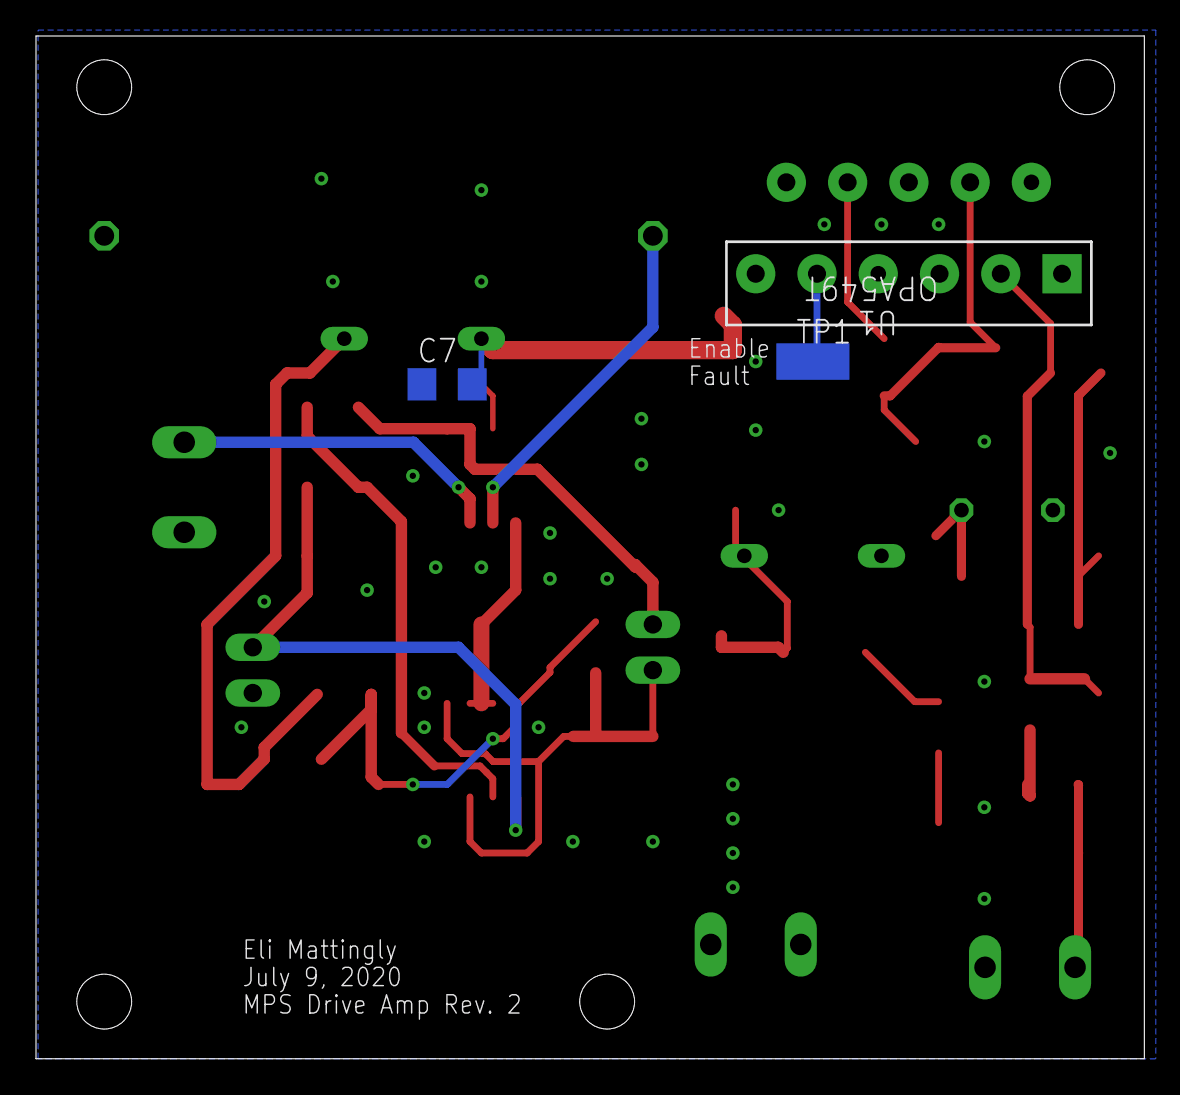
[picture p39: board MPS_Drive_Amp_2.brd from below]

Board: 2 copper layers, 61.6 x 56.8 mm, 51 parts (3 on the bottom side), 21 nets.

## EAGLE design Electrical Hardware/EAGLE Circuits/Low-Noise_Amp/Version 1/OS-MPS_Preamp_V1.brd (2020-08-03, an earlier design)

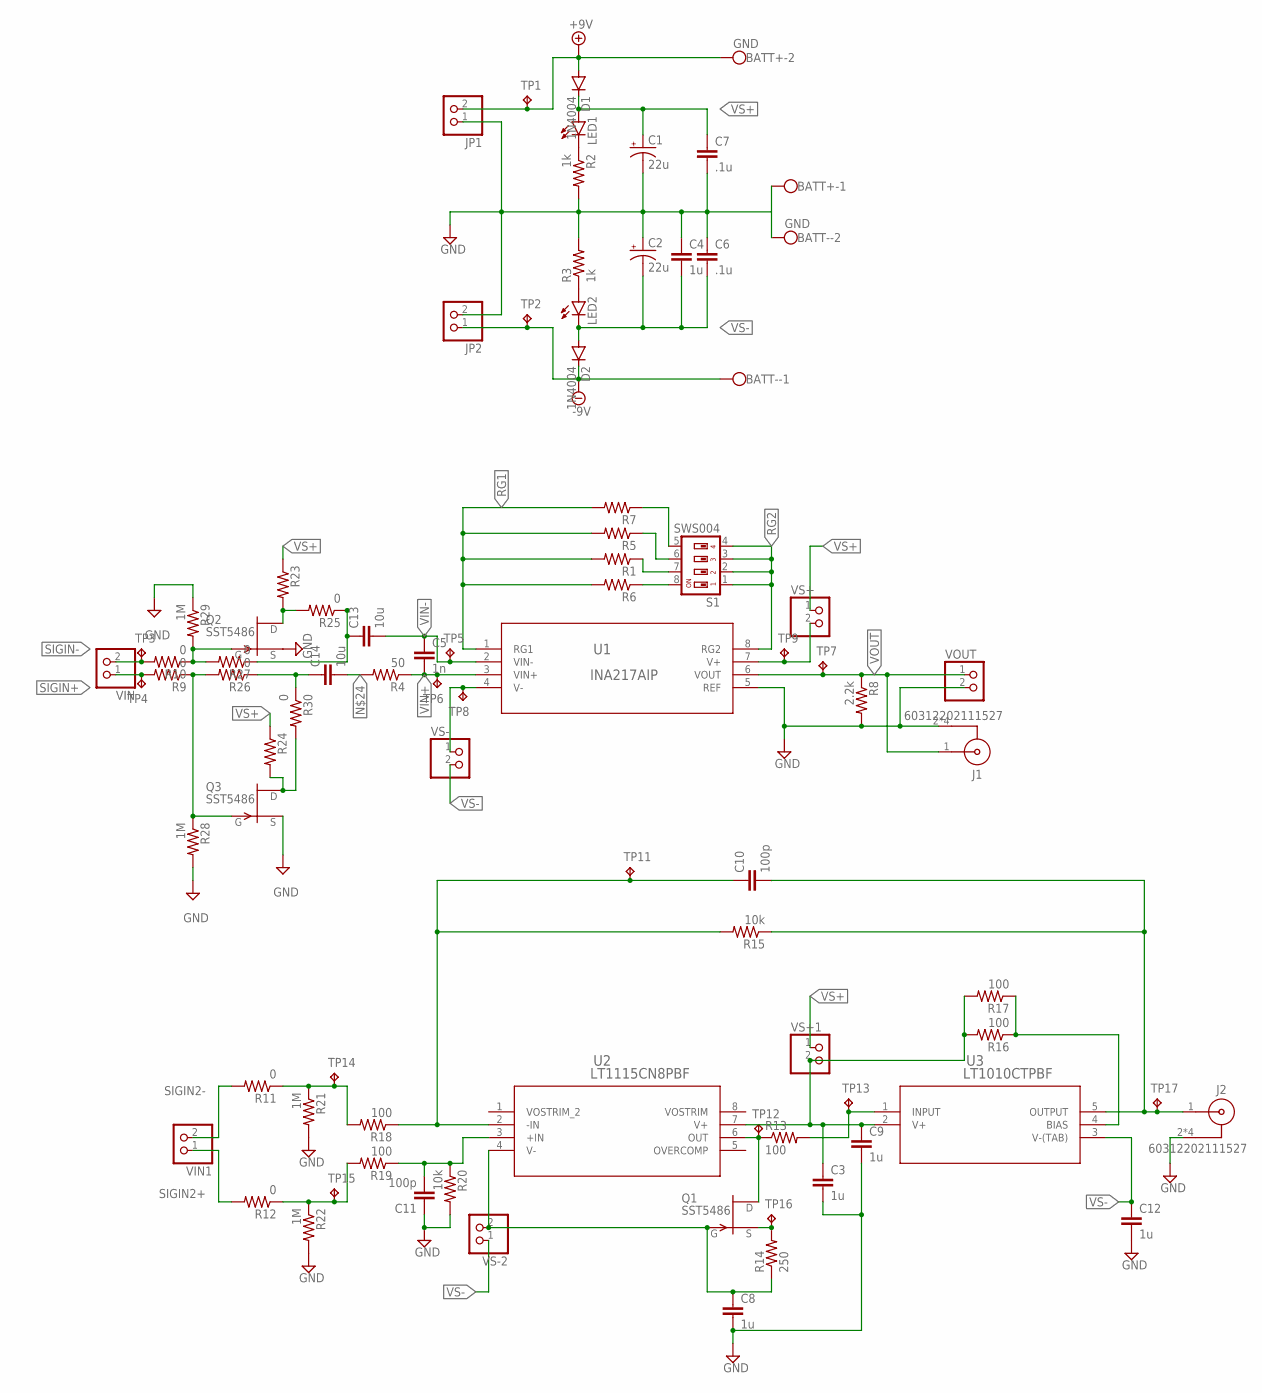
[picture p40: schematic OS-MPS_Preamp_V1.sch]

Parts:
BATT+: GND; W237-102
BATT-: GND; W237-102
C1, C2: 22u; TT2D6
C3, C4, C8, C9, C12: 1u; C1206
C5: 1n; C1206
C6, C7: .1u; C1206
C10, C11: 100p; C1206
C13, C14: 10u; C1206
D1, D2: 1N4004; DO41-10
J1, J2: 60312202111527
JP1, JP2: PINHD-1X2; 1X02
LED1, LED2: LEDSML0805; SML0805
Q1, Q2, Q3: SST5486; SOT23
R1, R5, R6, R7, R23, R24: R-US_R0805; R0805
R2, R3: 1k; R0805
R4: 50; R0805
R8: 2.2k; R0805
R9, R10, R11, R12, R25, R26, R27, R30: 0; R0805
R13, R16, R17, R18, R19: 100; R0805
R14: 250; R0805
R15, R20: 10k; R0805
R21, R22, R28, R29: 1M; R0805
S1: SWS004; SMS-004
TP1, TP2: TPB2,54; B2,54
TP3, TP4, TP5, TP6, TP7, TP8, TP9, TP11, TP12, TP13, TP14, TP15, TP16, TP17: TPTP20SQ; TP20SQ
U1: INA217AIP; P8
U2: LT1115CN8PBF; PDIP-8_N_LIT
U3: LT1010CTPBF; TO220-5_T
VIN, VIN1: PINHD-1X2; 1X02
VOUT: PINHD-1X2; 1X02
VS+, VS+1: PINHD-1X2; 1X02
VS-, VS-2: PINHD-1X2; 1X02

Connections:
+9V: BATT+.2, D1.A, JP1.2, TP1.TP
-9V: BATT-.1, D2.C, JP2.1, TP2.TP
GND: BATT+.1, BATT-.2, C1.-, C2.+, C3.2, C4.1, C6.1, C7.2, C8.2, C9.2, C11.1, C12.2, J1.2, J1.3 (2), J1.4 (2), J1.5 (2), J2.2, J2.3 (2), J2.4 (2), J2.5 (2), JP1.1, JP2.2, Q2.2 (S), Q3.2 (S), R2.2, R3.2, R8.2, R20.2, R21.2, R22.2, R28.2, R29.1, U1.5 (REF), VOUT.2
unnamed: LED1.C, R2.1
unnamed: TP9.TP, U1.7 (V+), VS+.2
unnamed: TP8.TP, U1.4 (V-), VS-.1
unnamed: R5.1, S1.6
unnamed: R1.1, S1.7
unnamed: R6.1, S1.8
unnamed: C11.2, R19.1, R20.1, U2.3 (+IN)
unnamed: R7.1, S1.5
unnamed: LED2.A, R3.1
unnamed: C8.1, Q1.3 (G), R14.1, U2.4 (V-), VS-2.2
unnamed: R11.1, R18.2, R21.1, TP14.TP
unnamed: Q1.1 (D), R13.1, TP12.TP, U2.6 (OUT)
unnamed: R13.2, TP13.TP, U3.1 (INPUT)
unnamed: Q1.2 (S), R14.2, TP16.TP
unnamed: R12.1, R19.2, R22.1, TP15.TP
unnamed: C10.2, J2.1, R15.1, TP17.TP, U3.5 (OUTPUT)
unnamed: C10.1, R15.2, R18.1, TP11.TP, U2.2 (-IN)
unnamed: R16.1, R17.1, U3.4 (BIAS)
unnamed: C3.1, C9.1, R16.2, R17.2, U2.7 (V+), U3.2 (V+), VS+1.2
unnamed: Q2.1 (D), R23.2, R25.2
unnamed: Q3.1 (D), R24.2, R30.2
unnamed: Q3.3 (G), R9.1, R26.2, R28.1
unnamed: Q2.3 (G), R10.1, R27.2, R29.2
unnamed: C14.2, R4.2
unnamed: C13.1, R25.1, R27.1
RG1: R1.2, R5.2, R6.2, R7.2, U1.1 (RG1)
RG2: S1.1, S1.2, S1.3, S1.4, U1.8 (RG2)
SIGIN2+: R12.2, VIN1.1
SIGIN2-: R11.2, VIN1.2
SIGIN+: R9.2, TP4.TP, VIN.1
SIGIN-: R10.2, TP3.TP, VIN.2
VIN+: C5.2, R4.1, TP6.TP, U1.3 (VIN+)
VIN+_1: C14.1, R26.1, R30.1
VIN-: C5.1, C13.2, TP5.TP, U1.2 (VIN-)
VOUT: J1.1, R8.1, TP7.TP, U1.6 (VOUT), VOUT.1
VS+: C1.+, C7.1, D1.C, LED1.A, R23.1, R24.1, VS+.1, VS+1.1
VS-: C2.-, C4.2, C6.2, C12.1, D2.A, LED2.C, U3.3 (V-(TAB)), VS-.2, VS-2.1

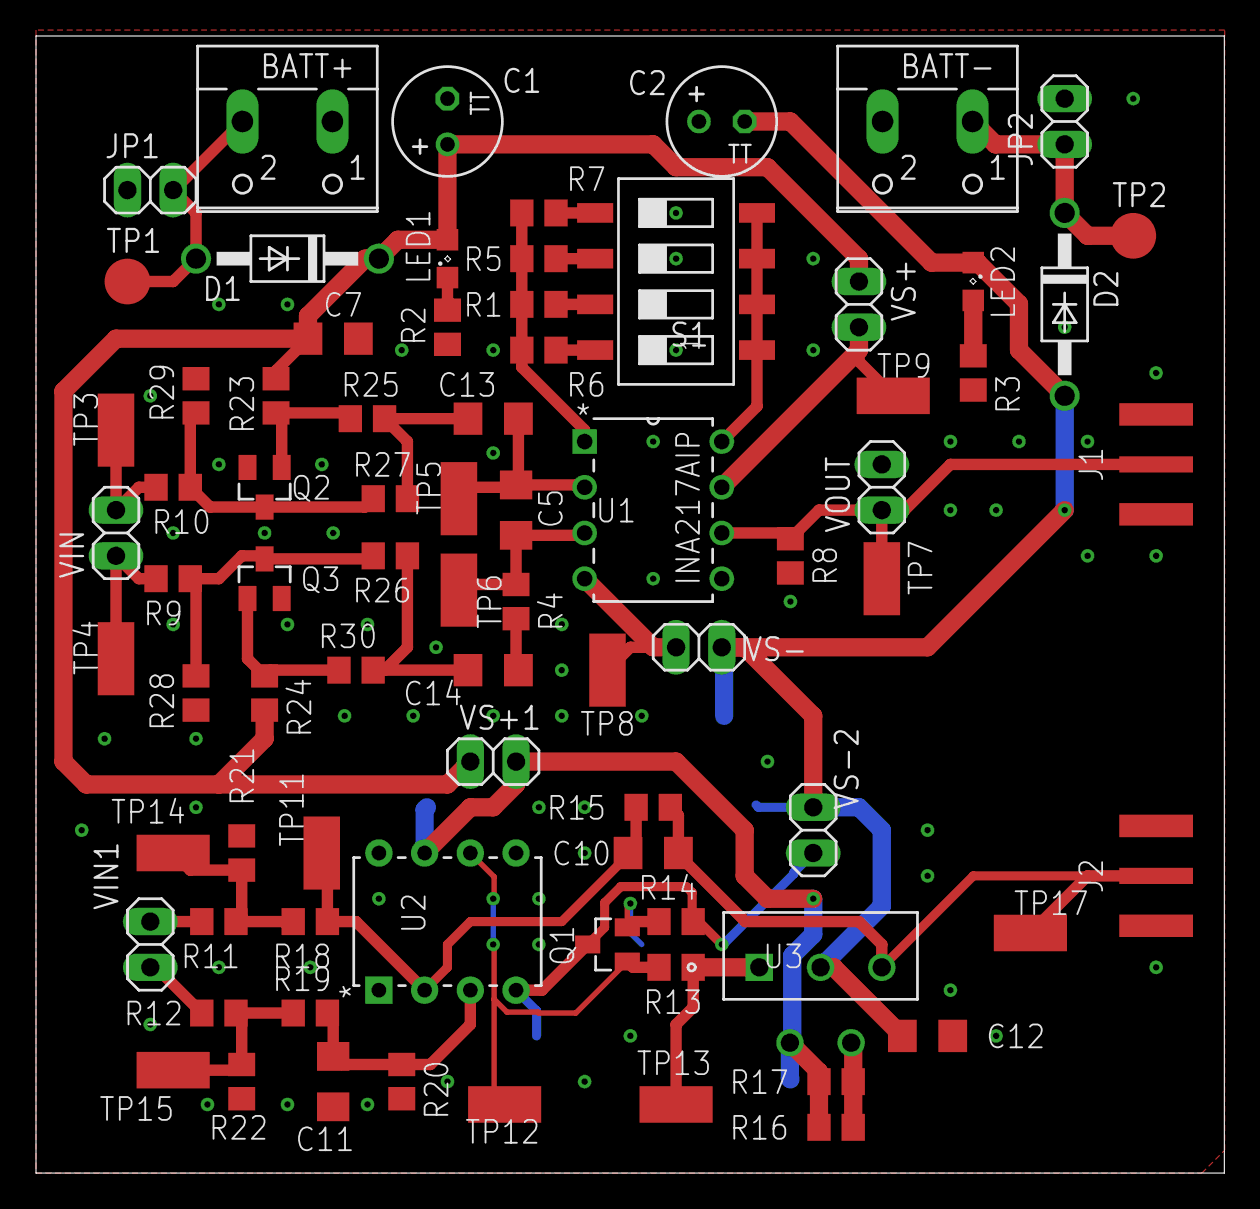
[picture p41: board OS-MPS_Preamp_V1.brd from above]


Board: 2 copper layers, 66.0 x 63.2 mm, 84 parts (6 on the bottom side), 40 nets.

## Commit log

2019-11-13 Create OSMPI Part Management-MPS.xlsx
    [OSMPI Part Management-MPS.xlsx]
2019-12-01 Updatet_Part sheet
    [OSMPI Part Management-MPS.xlsx]
2020-02-17 Initial Inventor Part Push
    [1310_Drive Coil Assm_V1.0002.iam, 1310_Drive Coil Assm_V1.iam, 1311_Drive Coil Main Body_V1.0001.ipt, 1311_Drive Coil Main Body_V1.ipt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]
2020-08-03 Electrical Documentation
    Add LT Spice and PCB files
    [MPS_Drive_Amp_2.brd, MPS_Drive_Amp_2.sch, OS-MPS_Preamp_V1.brd, OS-MPS_Preamp_V1.sch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]
2020-09-07 Update Scripts and BOM
    [OSMPI Part Management-MPS.xlsx]
2020-09-14 Update Inventor Files
    [1310_Drive Coil Assm_V2.iam, 1311_Drive Coil Main Body_V2.ipt, 1313_Drive Coil End_V2.ipt, 2101_Rx Coil Body_V2.ipt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]
2020-09-15 Update Inventor
    [1310_Drive Coil Assm_V1.iam, 1310_Drive Coil Assm_V2.0002.iam, 1310_Drive Coil Assm_V2.iam, 1311_Drive Coil Main Body_V1.ipt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]
2021-05-13 Add PCB BOM
    The BOM has been updated and PCB assembly files were added
    [AntiAlias Filter_Diff_Active.brd, AntiAlias Filter_Diff_Active.csv, AntiAlias Filter_Diff_Active.sch, MPS_Drive_Amp_2.csv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]
2021-05-13 Update OSMPI Part Management-MPS.xlsx
    [OSMPI Part Management-MPS.xlsx]
2021-05-19 Version 2 initial update
    Initial update of files
    [1000_Bias_Coil_Spacers_MPSv2_v1.iam, 1000_Coil_Positioning_Assembly_MPSv2_v4.iam, 1000_Full_Assembly_MPSv2_v2.iam, 1001_Bias_Coil_Holder_MPSv2_v2.iam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]
2021-05-19 Update Inventor Part files
    [1000_Coil_Positioning_Assembly_MPSv2_v4.0011.iam, 1000_Coil_Positioning_Assembly_MPSv2_v4.iam, 1002_Bias_Coil_MPSv2_v3.0008.iam, 1002_Bias_Coil_MPSv2_v3.iam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]
2021-05-20 Add Render and STEP file
    [1000_Coil_Positioning_Assembly_MPSv2_v4.0011.iam, 1000_Coil_Positioning_Assembly_MPSv2_v4.0012.iam, 1000_Coil_Positioning_Assembly_MPSv2_v4.iam]
2021-05-20 Update BOM for PreAmp
    [1000_Full_Assembly_MPSv2_v2.0013.iam, 1000_Full_Assembly_MPSv2_v2.iam, OSMPI Part Management-MPS.xlsx]
2021-06-06 Update Preamp Files
    Making them more compatible with fab.
    [OS-MPS_Preamp_V2_OnlyINA.csv, PnP_OS-MPS_Preamp_V2_OnlyINA_front.csv, copper_bottom.gbr, copper_top.gbr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]
2021-06-06 Update BOM/PnP
    [OS-MPS_Preamp_V2_OnlyINA_JLC_BOM.csv, PnP_OS-MPS_Preamp_V2_OnlyINA_front.csv]
2021-07-07 Update sample holder+AA filter
    [1000_Coil_Positioning_Assembly_MPSv2_v4.0012.iam, 1000_Coil_Positioning_Assembly_MPSv2_v4.0014.iam, 1000_Coil_Positioning_Assembly_MPSv2_v4.iam, 1000_Full_Asse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]
2021-07-08 Update CAD
    [6000_Sample Assembly_V2-Jul82021.stp, 6000_Sample Assembly_V2.0012.iam, 6000_Sample Assembly_V2.0014.iam, 6000_Sample Assembly_V2.iam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]
2021-07-08 Add STEP assembly
    [1000_Full_Assembly_MPSv2_v2.0016.iam, 1000_Full_Assembly_MPSv2_v2.0018.iam, 1000_Full_Assembly_MPSv2_v2.iam, 5010_1444-17154_[DigiKey]_Aluminum_Chasis_Modifica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]
2021-07-08 PCB Pictures
2021-11-02 Add KiCAD imported files
    [MPS_Drive_Amp_2.kicad_pcb, MPS_Drive_Amp_2.sch, OS-MPS_Preamp_V2_OnlyINA.kicad_pcb, OS-MPS_Preamp_V2_OnlyINA.sch]
2022-04-08 Bulb Holders
    [6103B_Bulb Arm_Microcentrifuge-tube-0,2mL.0002.ipt, 6103B_Bulb Arm_Microcentrifuge-tube-0,2mL.ipt, 6103B_Bulb Arm_Microcentrifuge-tube-0,2mL.stl, 6103_Bulb Arm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]
2022-10-12 Filter Demo files
2022-11-01 Add results, update readme
    [1000_Coil_Positioning_Assembly_MPSv2_v4.0011.iam]
2022-11-04 Reorganize files, archive old
    [1000_Bias_Coil_Spacers_MPSv2_v1.iam, 1000_Coil_Positioning_Assembly_MPSv2_v4.0011.iam, 1000_Coil_Positioning_Assembly_MPSv2_v4.0014.iam, 1000_Coil_Positioning_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]
2023-01-16 Revert "Merge branch 'master' of https://github.com/OS-MPI/MPS"
    This reverts commit 0830b3b2eac63f10c73bfe72329d2da439e7747c, reversing
    changes made to c0ffb2e8f59d7c4befeacfec3356fb3a495e5a89.
    [1000_Bias_Coil_Spacers_MPSv2_v1.iam, 1000_Coil_Positioning_Assembly_MPSv2_v4.0011.iam, 1000_Coil_Positioning_Assembly_MPSv2_v4.0014.iam, 1000_Coil_Positioning_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]
2023-01-16 Demo Cross Section
    [DemoCrossSect.0001.ipt, DemoCrossSect.ipt, DriveCoil-Litz_N22Each-20mmID.dxf]
2023-05-31 Inventor files
    [2000_Rx_Coil_Former_MPSv2_v2.ipt, 2002_Rx_Tx Coil Spacer_Glass_v3.ipt, 2002_Rx_Tx Coil Spacer_Glass_v3.stl, 2100_Tx_Coil_Assm_V1.iam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]
2024-03-21 Move parts to archive
    [1310_Drive Coil Assm_V1.0002.iam, 1310_Drive Coil Assm_V2.0002.iam, 1310_Drive Coil Assm_V2.iam, 1311_Drive Coil Main Body_V1.0001.ipt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]
2024-03-21 Updated inventor files
    [1221_Backside Angle Bracket_V5.0002.dwg, 1221_Backside Angle Bracket_V5.dwg, 2000_Rx_Coil_Former_MPSv2_v2.0004.ipt, 2100_Tx_Coil_Assm_V1.0001.iam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]
2024-03-22 Update inventor assm
    [1000_Coil_Positioning_Assembly_MPSv2_v4.0014.iam, 1000_Coil_Positioning_Assembly_MPSv2_v4.0015.iam, 1000_Coil_Positioning_Assembly_MPSv2_v4.iam, 1000_Full_Asse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]

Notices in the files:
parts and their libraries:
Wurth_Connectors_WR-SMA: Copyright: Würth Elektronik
